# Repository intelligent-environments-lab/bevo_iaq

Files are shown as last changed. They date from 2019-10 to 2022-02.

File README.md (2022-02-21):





# Bevo Beacon IAQ
This document details the basics of the Building EnVironment and Occupancy (BEVO) Beacon with enhanced Indoor Air Quality (IAQ) monitoring. 

## Installation

### 1. Install GIT and Clone Repository

Make sure your RPi is connected to WiFi. Then install git with

```bash
sudo apt install git
```

Clone this repository and `cd` into the newly created bevo `bevo_iaq` directory. Edit the `rpi_install.sh` file to include the correct GitHub credentials and set your timezone. 

### 2. Install Libraries to RPi

Run

```bash
sh rpi_install.sh
```

which will install updates, upgrade, install Python3, initialize the Tailscale VPN, and create a virtual environment. 

### 3. Install Libraries to Virtual Environment

Create a virtual environment with

```bash
source .venv/bin/activate
```

and then install the packages to operate the beacon's monitoring capabilities

```bash
pip install -r requirements.txt
```

### 4. Enable Service Files on Boot

Finally, enable the service files by

```bash
deactivate
```

```bash
sh service_install.sh
```

### 5. Specify Device Number (Optional)

By default, the device number is 00. You can specify the number by running the `fix_number` shell script:

```bash
sh fix_number.sh <label>
```

where `<label>` is any identifier you would like whether it be numeric, alphabetical, or a combination.

### 6. Finalize and Check

Simply restart with `$ sudo reboot` for a clean start to the device.

You can check if the device is working properly by examining the data in the `DATA` directory or on the individual services with:

```bash
sudo journalctl -u <service_name>.service
```

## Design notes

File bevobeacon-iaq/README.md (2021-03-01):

# BEVO Beacon IAQ Setup 

 The following sections detail how to setup the different components of the BEVO Beacon IAQ. Each section should be completed in the order written. 

## Raspberry Pi 3|B+
 This file outlines the basics of setting up a Raspberry Pi 3|B+ (RPi), outlining the necessary components/libraries needed, how to install the Raspbian Buster Lite Operating System (OS), and how to set up the OS properly. 

 RPi3

 ### Necessary Components
 The necessary components are as follows:
 - Rapsberry Pi 3|B+
 - Power supply (micro USB)
 - HDMI cable
 - microSD card
 - microSD card reader

 ### Installing Raspbian Buster Lite
 The OS can be found on Raspberry Pi's website [here](https://www.raspberrypi.org/downloads/raspbian/). There are multiple options, but Raspbian Buster Lite utilizes a no-nonsense, command line interface. 

 1. Download Raspbian Bust Lite from the Raspberry Pi website
   - Website link is in the description above
   - Download the latest zip file
 2. Flash the file onto the SD card
   - Etcher can flash the zip file onto the SD card
 3. Check if installation was successful 
   - Insert flashed SD card
   - Connect RPi to monitor via HDMI
   - Power up the RPi
   - Check to see if the RPi goes through the different power on protocols

 ### Connecting to WiFi
 The RPi 3|B+ has built-in WiFi capabilities meaning you can immediately connect your RPi to the internet. 

 1. From the command line on the RPi, navigate to the directory ```/etc/wpa_supplicant/``` and edit the *wpa_supplicant.conf* file.
 2. Add the following lines to set up a network, replacing the text in quotations with the name of your network and password:
 ```
 network={
   ssid="<NAME _OF_NETWORK>"
   psk="<PASSWORD_FOR_NETWORK>"
 }
 ```
 3. Perform a reboot with ```$ sudo shutdown -r now``` or ```$ sudo reboot```
 4. Check to see if the RPi connects to WiFi - there should be an IP address specified when rebooting

 ### Special Considerations for Connecting to utexas-iot WiFi
 If connecting to the utexas-iot network, additional steps are required before the first step in the previous section:

 1. From the command line on the RPi, type "ifconfig" and copy down the ethernet MAC address under "wlan0" 
 2. Navigate to UT's network [page](https://network.utexas.edu)
 3. Login with your UT EID and password
 4. Click "Register Wireless Device"
 5. Enter the MAC address you copied down earlier, give the device a name, and register
 6. A textbox will appear with the devices password. Now when you edit *wpa_supplicant.conf* in step 2 above, use "utexas-iot" as the ssid name and enter the password inside quotation marks with **no spaces** for the password. 
 
### Attaching to Virtual Private Network (VPN)

#### Logmein Hamachi
The older generations of the BEVO Beacons were connected to users through the Logmein Hamachi VPN. 

##### Resources
1. [General Process](https://medium.com/@KyleARector/logmein-hamachi-on-raspberry-pi-ad2ba3619f3a)
2. [Exception when using RPi Zero](https://community.logmein.com/t5/LogMeIn-Hamachi-Discussions/Raspberry-Pi-quot-illegal-instruction-quot/td-p/201479)

#### Tailscale
Tailscale is a similar version to Logmein Hamachi, but a free, more simplified version. 

##### Resources
1. [Installing](https://tailscale.com/kb/Install)
1. [Installing on RPi](https://tailscale.com/kb/1043/install-raspbian-buster)
2. [Using Auth Keys](https://tailscale.com/kb/1085/auth-keys)

 ### Update RPi OS and Python
 Run the two lines below:
 ```
 $ sudo apt-get update
 $ sudo apt-get upgrade
 ```
 then install pip and pip3 installer:
 ```
 $ sudo python get-pip.py
 $ sudo apt-get install python3-pip
 ```
 and upgrade setup tools:
 ```
 $ sudo pip3 install --upgrade setuptools
 ```

 ### Enable I2C and SPI
 Install supporting dependencies:
 ```
 $ sudo apt-get install -y python-smbus
 $ sudo apt-get install -y i2c-tools
 ```

 Both can be enabled via ```$ sudo raspi-config``` by selecting the appropriate communication from the interfaceing options. More detailed instructions (they are short) can be found at the following links:
 - [I2C](https://learn.adafruit.com/adafruits-raspberry-pi-lesson-4-gpio-setup/configuring-i2c)
 - [SPI](https://learn.adafruit.com/adafruits-raspberry-pi-lesson-4-gpio-setup/configuring-spi)

### Cloning GitHub Repository
 Once connected to WiFi, using a GitHub repository makes updating and sharing files easy between two systems and others. The following steps will help to ensure that you can clone your GitHub repository to the RPi and start using git. 

 1. Check the Date
   - GitHub commands make queries that rely on the RPi having the correct time. 
   - Type ```$ date -R``` and make sure the time is correct. If the time is incorrect, type ```$ sudo apt-get install ntp```.
   This will allow the RPi to update the time. Be sure to do a ```$ sudo reboot``` after so the changes can take effect.
 2. Navigate to GitHub and copy down this repository's address.
 3. On the RPi install the git commands with ```$ sudo apt-get install git-core```
 4. Once installed, type ```$ git clone <GIT ADDRESS>``` to clone the repository on to the RPi.
 5. Move into the new directory and type ```$ git status``` to see if the clone worked correctly. 

 This repository holds all the necessary code needed to run the BEVO IAQ Sensor Platform. After setting up the Raspberry Pi, installing the necessary dependencies, and making all the hardware connections - the platform should be ready to go. 
 
### Installing Necessary Sensor Packages/Libraries
In addition to the packages specified above, the following set of packages have to be installed on to the RPi to use the current version of the code. 

#### Adafruit Sensors
To allow use of the adafruit sensors, one needs to run the following two commands:

**Light Sensor** ([TSL2591](https://www.adafruit.com/product/1980))
```
$ sudo pip3 install adafruit-circuitpython-tsl2591
```

**TVOC Sensor** ([SGP30](https://www.adafruit.com/product/3709))
```
$ sudo pip3 install adafruit-circuitpython-sgp30
```

**OLED Screen** ([SSD1306](https://learn.adafruit.com/micropython-hardware-ssd1306-oled-display/circuitpython))
```
# sudo pip3 install adafruit-circuitpython-ssd1306
```

#### Sensirion
To use the Sensirion sensors, one needs to install the following packages:

**Pi GPIO** ([Documentation](http://abyz.me.uk/rpi/pigpio/python.html))
```
$ sudo apt-get install python-pigpio
```
The Pi GPIO needs to be activiated on every boot of the RPi, so to ensure that this happens each time you can edit the bash file. From anywhere, type:
```
$ sudo nano ~/.bashrc
```
At the bottom of the file, add the two lines of code:
```python
# To activate Pi GPIO
sudo pigpiod
```

**Checksum** ([Documentation](http://crcmod.sourceforge.net/crcmod.html#module-crcmod))
```
$ sudo apt-get install python-crcmod
```

### Using Amazon Web Services
First to use Amazon Web Services (AWS), we need to install a few packages. For AWS to work with both sensor brands, we need use both versions of pip to get it to work for Python 2 and 3. 
```
$ sudo pip install boto3
$ sudo pip3 install boto3
```

The code supports the use of RPi profiles which means one must edit the ```/etc/profile``` of the RPi. The following lines should be added to the bottom of the file, with your appropriate string value within the angled brackets:
```C
export AWS_ACCESS_KEY_ID='<AWS_ACCES_KEY_ID>'
export AWS_SECRET_ACCESS_KEY='<AWS_SECRET_ACCESS_KEY>'
export BUCKET_NAME='<BUCKET_NAME>'
```

**NOTE**: You must type the above lines EXACTLY as you see them. Any extra spaces added will make the exports unusable. 
 
## Sensor Hardware Connection
The next few sections outline how to connect the sensors to the RPi. 

### Prototyping
The schematic below shows one possible way to connect the sensors to the RPi via breadboard. From left to right in the schematic, the sensors represented are: SCD30, SVM30, SPS30, TSL2591, and RTC PCF8523. *Note: The sensors used in the schematic are NOT exact replicas.*

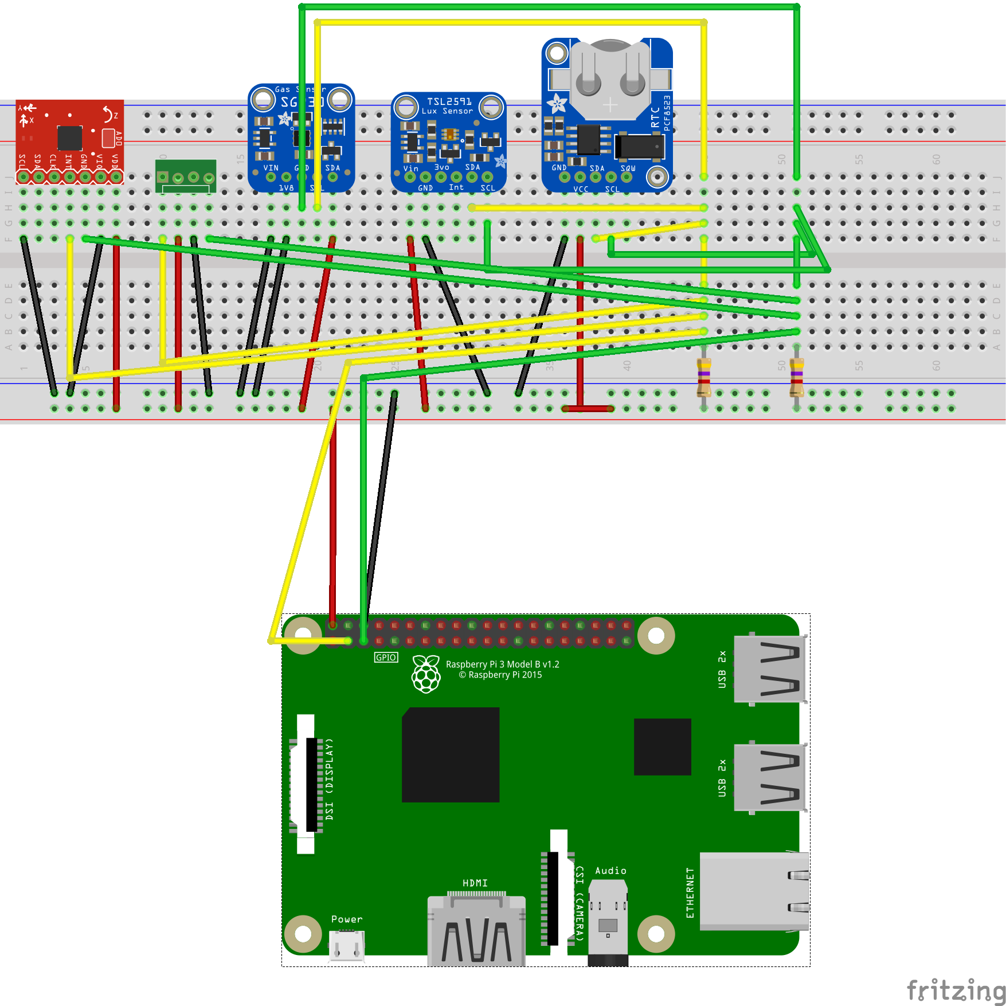
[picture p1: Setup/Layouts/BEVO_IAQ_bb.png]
bevo_iaq_bb


### Printed Circuit Board
A printed circuit board (PCB), shown below, was developed for this project. The PCB design does *not* allow for any direct connections to the board via headers except for the the RTC PCF8523 - the other sensors must be connected with wires.

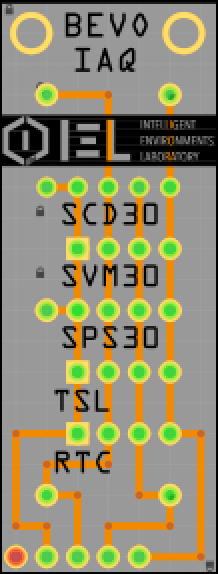
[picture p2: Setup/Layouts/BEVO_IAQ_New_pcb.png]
bevo_iaq_pcb


The sensors in the schematic above are labeled, and from top to bottom are:
1. SCD30 - Carbon Dioxide, Temperature, and Relative Humidity
2. SVM30 - Total Volatile Organic Compounds
3. SPS30 - Particulate Matter
4. TSL2591 - Light
5. PCF8523/DS1307 - Real-Time Clock
6. SSD1306 - OLED Screen

The remaining sensors are be connected with female-to-female wires after soldering male-to-male header pins to both the PCB and each individual sensor. The PCB in the schematic shows the top view where the connections are routed on the bottom of the board. There are five columns of connections on the PCB. From left to right, these columns represent specific pin connections:
1. Extra GND connection - needed for SCD30 and SPS30 SEL pins
2. GND connection
3. Vin connection
4. Serial Data (SDA) connection
5. Serial Clock (SCL) connection

Two 4.7 k-Ohm resistors are connected at the top and bottom as pull-up resistors. 

The SVM30 and SPS30 are connected through the use of [5-pin female single connectors](https://images-na.ssl-images-amazon.com/images/I/41WAqkLeBJL._SL500_AC_SS350_.jpg) and [4-pin female single connectors](https://images-na.ssl-images-amazon.com/images/I/411g-Ag85ML._SL500_AC_SS350_.jpg), respectively.

For the remaining sensors, wires are cut, crimped, and plugged in with the following specifications:
1. **SCD30**
 - Wires: blue, black, red, yellow, and green wires each cut to a length of 3 inches
 - Female to Female connections:
  - PCB Connection: 5x1 blue, black, red, yellow, green
  - Sensor Connection: 4x1 red, black, green, yellow; 1x1 blue
 - i2c Address: 61
 - Layout:
 
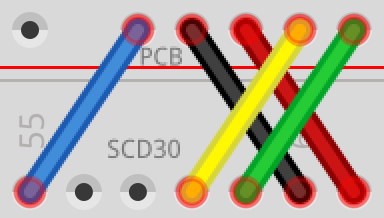
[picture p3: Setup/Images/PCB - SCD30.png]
pcb-scd30
 
 
 2. **SVM30**
 *Note: Connectors are provided - wires do not need to be crimped*
 - Wires: red, white, yellow, black
 - Wire to connector
 - i2c Address(es): 58 and 70
 - Layout: 
 
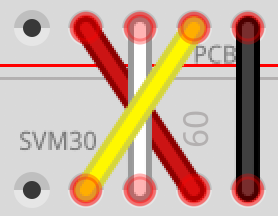
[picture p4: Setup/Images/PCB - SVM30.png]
pcb-svm30
 
 
 3. **SPS30**
 *Note: Connectors are provided - wires do not need to be crimped*
 - Wires: red, black, navy, green, yellow
 - Wire to connector
 - i2c Address(es): 69
 - Layout: 
 
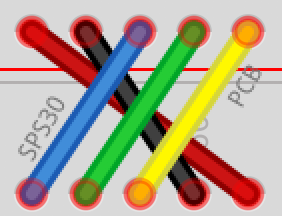
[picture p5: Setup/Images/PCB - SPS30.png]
pcb-sps30
 
 
 4. **TSL**
 - Wires: black, red, yellow, green
 - Female to Female connections
  - PCB Connection: 4x1 black, red, yellow, green
  - Sensor Connection: 2x1 red, black; 2x1 yellow, green 
 - i2c Address: 29
 - Layout: 
 
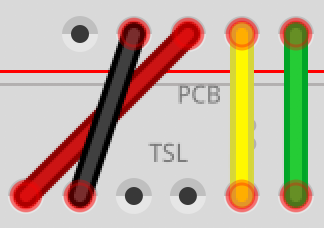
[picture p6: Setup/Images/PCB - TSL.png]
pcb-tsl
 
 
 5. **RTC**
 - Wires: black, red, yellow, green
 - Female to Female connections
  - PCB Connection: 4x1 black, red, yellow, green
  - Sensor Connection: 4x1 red, black, yellow, green
 - i2c Address: 68 (changes to UU once connected)
 - Layout:

 6. **OLED**
 - Wired: black, red, yellow, green
 - Female to Female connections
  - PCB Connection: 4x1 black, red, yellow, green
  - Sensor Connection: 4x1 red, black, yellow, green
 - i2c Address: 3c
 - Layout:

 6. **RPi**
 - Wires: black, red, yellow, green
 - Female to Female connections
  - PCB Connection: 4x1 red, black, yellow, green
  - RPi Connection: 5x2 (top row) red, red (fan), black, space, space (bottom row) space, yellow, green, space, black
 - Layout:
 
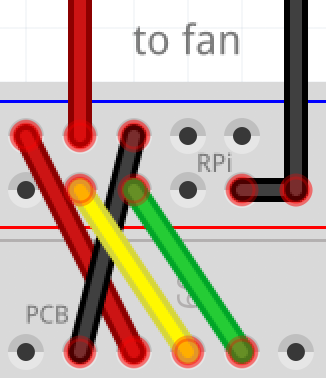
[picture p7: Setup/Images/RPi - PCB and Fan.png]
rpi-pcb
 

### Real-Time Clock Setup
The link to setup three different real-time clocks is found [here](https://learn.adafruit.com/adding-a-real-time-clock-to-raspberry-pi/set-rtc-time). 

## Code Development
(Under Construction)

### Running Code on Startup
With the code ready to run, we can enable it to run on boot of the RPi. To do so we can create service files that are run during the normal power-on process. 
1. Create the .service files (there are three such files in located [here](https://github.com/intelligent-environments-lab/bevo_iaq/tree/master/Setup/Code)
2. Place the .service files in the ```/etc/systemd/system/``` directory
3. You can test your service files before enabling them by typing ```$ sudo systemctl start your_service.service``` and then you can stop the test by typing ```$ sudo systemctl stop your_service.service```
4. Once you are ready, enable the service by typing ```$ sudo systemctl enable your_service.service```
5. Reboot your RPi and the service should run on boot in the background. 

See [here](https://www.raspberrypi.org/documentation/linux/usage/systemd.md) for ruther reading.

## Calibration
(Under Construction)
Due to the nature of low-cost sensors, calibration needs to occur in order to improve their accuracy. 

### SPEC Sensor Initial Calibration
The SPEC sensors need an initial calibration to identify the sensitivity factor. Since the SPEC sensors are the only sensors using serial communication, we have to use a program like [picocom](https://linux.die.net/man/8/picocom) to communicate with them. The following steps allow you to view the output of the SPEC sensors:
1. The SPEC sensors are connected via USB so check to see if they are any USB devices by typing either ```$ lsusb``` or changing into the ```/dev/``` directory and listing all directories/files. In the first case, you should see two devices that start with the name "Cyngal Integrated Products". In the latter, look for "ttyUSB0" and "ttyUSB1" in the ```/dev/``` directory.
2. Use picocom to connect to one of the USB devices (0 or 1) with:
```$ sudo picocom /dev/ttyUSB0```
3. You can check which sensor you are communicating with by typing "e"
4. These sensors need a continuous source of power to function most effectively. When you initially connect them, you should let them run for at least an hour or until the concentration has settled out. To see the measurement values, you have two options:
 1. Pressing enter will return one measurement
 2. Typing "c" will start the continuous measurement, and values will be reported every second.
5. The output is the following: serial number, concentration (ppb), temperature (C), relative humidity, raw value 1, raw value 2, raw value 3, number of days, then hours, then minutes, then seconds that the sensor has been on. 
6. Type "c" and check to see that the concentrations are in relative agreement. If this is the case, you can type "r" to get out of continuous measurement. 
7. If the concentration is stable, you have two options: zero the sensor or specify the concentration in the room:
 1. If the concentration of the pollutant is zero, type "Z" to zero the sensor.
 2. if the concentration of hte pollutant is known, type "S XXX" with the known concentration in ppm.

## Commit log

2019-10-07 Added the layouts from bevobeacon2.0
    [BEVO_IAQ.fzz, SCD30.fzz, SGP30.fzz, SHT31D.fzz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]
2019-10-07 Moved layouts
    [BEVO_IAQ.fzz, SCD30.fzz, SGP30.fzz, SHT31D.fzz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]
2019-10-07 Logged some data
    [scd30_2019-10-7_18-48-2.csv, tsl2591_2019-10-7_18-49-40.csv]
2019-10-08 Included rtc layout
    [PCF8523.fzz]
2019-10-14 Updated the layout of the PCB
    [BEVO_IAQ.fzz, BEVO_IAQ_contour.gm1, BEVO_IAQ_copperBottom.gbl, BEVO_IAQ_copperTop.gtl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]
2019-10-21 Moved bevo iaq pcb milling file sto separate directory
    [BEVO_IAQ_New_contour.gm1, BEVO_IAQ_New_copperBottom.gbl, BEVO_IAQ_New_copperTop.gtl, BEVO_IAQ_New_maskBottom.gbs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]
2019-10-21 Added fritzing file for tsl
    [TSL2591.fzz]
2019-10-21 created image of PCB
    [BEVO_IAQ.fzz, BEVO_IAQ_New.fzz, BEVO_IAQ_contour.gm1, BEVO_IAQ_copperBottom.gbl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]
2019-10-21 Added section about connecting the sensors
2019-10-21 Added section about PCB design
2019-10-22 Created cleaner pcb
    [BEVO_IAQ_New.fzz, BEVO_IAQ_New_copperBottom.gbl, BEVO_IAQ_New_copperTop.gtl, BEVO_IAQ_New_maskBottom.gbs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]
2019-10-22 allowed pip for Python 2.7
    [tsl2591_2019-10-8_9-6-56.csv]
2019-10-23 some initial dummy data
    [2019-10-22_sensirion.csv]
2019-10-25 Updated printing and calculation method for pm
2019-10-29 collected data
    [2019-10-23_sensirion.csv, 2019-10-24_sensirion.csv, 2019-10-25_sensirion.csv, 2019-10-27_sensirion.csv]
2019-10-30 MORE DATA
    [2019-10-29_sensirion.csv, 2019-10-30_sensirion.csv]
2019-11-01 Logged more data
    [2019-10-30_sensirion.csv, 2019-10-31_sensirion.csv, 2019-11-01_adafruit.csv, 2019-11-01_sensirion.csv]
2019-11-01 removed old code from log and added old print human
2019-11-04 Added a print to see the bytes
2019-11-04 Added more data
    [2019-11-01_adafruit.csv, 2019-11-01_sensirion.csv, 2019-11-02_adafruit.csv, 2019-11-03_adafruit.csv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]
2019-11-06 Laser cutting files
2019-11-06 removed error printing
2019-11-06 used correct printhuman
2019-11-13 Created arduino code
2019-11-13 Updated printing
2019-11-15 Trying to set up spec sensors
2019-12-04 Removed clock and added Spec sensor basics
2019-12-05 removed single sensor
2019-12-05 Added wiring images
2019-12-09 removed old files
    [2019-10-22_sensirion.csv, 2019-10-23_sensirion.csv, 2019-10-24_sensirion.csv, 2019-10-25_sensirion.csv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]
2019-12-09 removed uncessary and added correct laser cutting files
2019-12-09 added dgs sensor logging
2019-12-10 Updated laser cutting files
2019-12-11 Updated dictionary
    [BeaconIAQ_PartList.xlsx]
2019-12-11 changed data logging interval for test
    [2019-12-09_adafruit.csv, 2019-12-09_sensirion.csv, 2019-12-10_adafruit.csv, 2019-12-10_sensirion.csv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]
2019-12-11 Included calibration section with SPEC initial calibration
2019-12-11 Included service files in the repo
    [2019-12-11_sensirion.csv]
2019-12-11 logged new data
    [2019-12-11_adafruit.csv, 2019-12-11_sensirion.csv]
2019-12-11 renamed directory
    [BeaconIAQ_PartList.xlsx]
2019-12-11 removed RPi storage on bevo_iaq
    [2019-12-09_adafruit.csv, 2019-12-09_sensirion.csv, 2019-12-10_adafruit.csv, 2019-12-10_sensirion.csv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]
2019-12-11 moved files
    [BeaconIAQ_PartList.xlsx]
2019-12-11 fixed bug and attach works now
2019-12-17 Updated the IAQ beacon part list
    [BeaconIAQ_PartList.xlsx]
2020-01-04 updated new logging for sensirion sensors
2020-01-08 created wiring for sps30 testing
    [SPS30.fzz]
2020-01-11 new laser uctting file
2020-01-31 updated log_2
    [IAQBeacon_Checklist.xlsx]
2020-02-16 changed log frequency
    [IAQBeacon_Checklist.xlsx]
2020-12-22 to csv
    [known_addresses.csv, known_addresses.xlsx]
2020-12-26 added addresses
    [known_addresses.csv]
2020-12-26 removed print
2020-12-27 added check data
    [known_addresses.csv]
2021-01-22 added correction to display
    [co2-linear_model-wcwh_s20.csv]
2021-03-09 Add print statements for debugging
2021-03-12 Separate code based on sensor
2021-03-12 Mute print statements and remove unused py files
2021-03-18 Switch sensirion sensors on and off between measurements
2021-04-10 included board
2021-04-13 including correction factors
    [co-linear_model-ux_s20.csv, co2-linear_model-wcwh_s20.csv, no2-linear_model-ux_s20.csv, pm2p5_mass-linear_model-wcwh_s20.csv]
2021-04-16 cleaned up
    [known_addresses.csv]
2021-06-21 updated for demo
    [co2-linear_model-wcwh_s20.csv, co2-linear_model-wcwh_s21.csv, no2-linear_model-ux_s20.csv, no2-linear_model-wcwh_s21.csv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]
2021-07-20 LED for connection
2022-02-21 s3 configuration
    [co-linear_model-ux_s20.csv, co2-linear_model-wcwh_s21.csv, no2-linear_model-wcwh_s21.csv, pm10_mass-linear_model-wcwh_s21.csv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]
2022-05-31 latest calibration data
    [co-constant_model-ux_s20.csv, co-linear_model-wcwh_s21.csv, co2-linear_model-ux_s20.csv, co2-linear_model-wcwh_s21.csv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]
2022-06-16 print on debug mode only
2022-06-16 removed print statements

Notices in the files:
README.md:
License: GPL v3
